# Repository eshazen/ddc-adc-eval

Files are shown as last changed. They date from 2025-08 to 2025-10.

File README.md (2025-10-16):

# ddc-adc-eval

Evaluation board for DDC112 ADC (Arduino UNO shield?).
See `led-photodiode-avr` design for working board.

## Notes from DDC112 datasheet:

* CLK freq range 1-10MHz
* Can generate 8MHz easily using AVR CTC
  <br>Conversion rate then 1.6kHz max
* It is recommended CONV toggle within ±10ns of the rising edge of CLK
* Mode (Cont vs Ncont) selected by state of CONT pin at power-up
  <br>can also switch based on T(INT): space between CONV edges > 4794 clocks
  (600uS at 8MHz clock)
* Data ready at ~526uS at 8MHz (4208 clocks)

## Readout strategy

* Readout function takes ~32us for 20 bits
* So maybe use CONV period of 558 + 10us (568us or 4544 clocks - 9088 period)

## Version 2 ECOs

### Main board

* Add transistors, expand to support 8 LEDs
* Change to common anode configuration (incl connector pinout)
* Correct external caps on DDC (2 -> 4 C's)
* Add 12 bit ADC for temperature sensor
* Testpoints?

### Optical board

* Fix photodiode pinout
* Add temp sensor next to photodiode on copper pad
* Add two Marubeni footprints next to D1 and D3
* Wire 8 LED drivers to the 9 LEDs with a jumper to choose between e.g. D3 and one Marubeni channel.
* Change to common anode topology
*

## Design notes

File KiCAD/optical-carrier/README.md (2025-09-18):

# optical-carrier

Simple carrier board for one photodiode and 3 LEDs.

## ECOs

* Photodiode wiring is reversed from the "obvious" orientation.

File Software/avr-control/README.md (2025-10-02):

# avr-control

Interactive CLI for testing the hardware.
This version uses interrupt-driven UART transmit to allow
continuous data acquisition.
```
    T [n]         - start timers with CONV period=n default 10000
    G n           - set integrator range 0-7
    C n           - enable/disable charge test mode
    A [d [a]]     - stream data at 800/d Hz average a samples
    L d           - set LEDs
    R             - read ADC repeatedly
    P             - read ADC and print
    D n           - set DAC
    M en ch       - set mux en=0/1 ch=0..7
    F             - capture fast and display
    ---
    W t r [d...]  - write I2C
```
Some notes:

* 'A' has a few options:
```
    A          output at default 1Hz, average 800 samples
	A 100      output at 800/100 = 8Hz, average 100 samples
	A 800 1    output at 1Hz, no averaging
```
* 'P' captures and displays data at about 1HZ.
<br>It always captures with the same phase of CONV
* 'F' captures 100 samples at the max rate continuously
<br>When any UART rx is seen, it stops and dumps the data
<br>The last column is the state of CONV (integrator A/B)

## Enhancements for further testing

Readout rate with T = 10000 should be exactly 1.6kHz.

After discussion with Lina:

New readout mode.  Variable rate from 100Hz to .02Hz.
Average up to 2^12 samples.

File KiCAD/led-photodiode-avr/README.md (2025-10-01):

# led-photodiode-avr

This is a test board with a 3-channel constant-current LED driver,
two-channel DDC112 ADC and an ATMega328 MCU.

An interactive CLI for testing is available in
`software/avr-clock-test`.

## Testing

Board#1 is in Lina's hands

Board#2 stuffing

* C1, C15 MIA so installed 0.47uF in place of 0.33uF

Running now.

T = 9800 works well

## ECOs

* External cap wiring incorrect.  For channel 1 two caps are needed,
on pins (3,4) and (5,6).  Same for channel 2

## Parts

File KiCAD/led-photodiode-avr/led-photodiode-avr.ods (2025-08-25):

Reference | Qty | Value | DNP | DigikeyNumber | ManufacturerNumber | 3xQty | OrderQty
C1,C15 | 2 | 0.33uF |  | 1276-1123-1-ND | CL21B334KBFNNNE | 6 | 10
C2,C4,C7,C9,C11,C13 | 6 | 10uF |  | 1292-0805X106K250CT-ND | 0805X106K250CT | 18 | 20
C3,C8 | 2 | 22uF |  | 1276-CL21A226MAYNNNECT-ND | CL21A226MAYNNNE | 6 | 10
C5,C6,C10,C12,C14,C16,C18,C22,C23,C54,C55 | 11 | 0.1uF |  | 478-KGM21NR71H104KTCT-ND | KGM21NR71H104KT | 33 | 50
C17 | 1 | 120pF |  | 399-C0805C121J3GACTUCT-ND | C0805C121J3GACTU | 3 | 10
C21 | 1 | 1nF |  | 399-C0805C102J5GACTUCT-ND | C0805C102J5GACTU | 3 | 10
C52 | 1 | 1.0uF |  | 1276-1029-1-ND | CL21B105KBFNNNE | 3 | 10
D1,D2,D3 | 3 | LED |  | 1516-QBLP631-R3ACT-ND | QBLP631-R3A | 9 | 15
J1 | 1 | Screw_Terminal_01x02 |  | A98076-ND | 282836-2 | 3 | 3
J2 | 1 | Conn_02x08_Odd_Even |  | 10129381-916001BLF-ND | 10129381-916001BLF | 3 | 3
J3 | 1 | ISP |  | 952-2092-ND | M20-9950345 | 3 | 3
L1,L2 | 2 | 10uH |  | 445-6762-1-ND | MLZ2012N100LT000 | 6 | 10
Q1,Q2,Q3,Q4 | 4 | TTC1949 |  | TTC1949-GRLFCT-ND | TTC1949-GR,LF | 12 | 12
R1 | 1 | 10k |  | P10KACT-ND | ERJ-6GEYJ103V | 3 | 10
R2,R10,R47 | 3 | 1.5k |  | 541-4161-1-ND | CRCW08051K50FKEAC | 9 | 20
R3,R5,R6 | 3 | 1k |  | 541-1.00KCCT-ND | CRCW08051K00FKEA | 9 | 20
R4 | 1 | 442 |  | 311-442CRCT-ND | RC0805FR-07442RL | 3 | 10
R7 | 1 | 24.9 |  | 541-CRCW120624R9FKEAHPCT-ND | CRCW120624R9FKEAHP | 3 | 10
R8,R9,R45 | 3 | 4.7k |  | 541-4131-1-ND | CRCW08054K70FKEAC | 9 | 20
U1 | 1 | REF3040AIDBZT |  | REF3040AIDBZTCT-ND | REF3040AIDBZT | 3 | 3
U2,U10 | 2 | AZ1117CH2-5.0 |  | 31-AZ1117CH2-5.0TRG1CT-ND | AZ1117CH2-5.0TRG1 | 6 | 10
U5 | 1 | DDC112 |  | 296-DDC112U/1KCT-ND | DDC112U/1K | 3 | 3
U6 | 1 | LTC1380 |  | 505-LTC1380CS#PBF-ND | LTC1380CS#PBF | 3 | 5
U7 | 1 | ATmega328-A |  | ATMEGA328P-AU-ND | ATMEGA328P-AU | 3 | 3
U8, U3 | 2 | OPA365AIDR |  | 296-46162-1-ND | OPA365AIDR | 6 | 6
U9 | 1 | LTC2631 |  | LTC2631CTS8-HZ12#TRMPBFCT-ND | LTC2631CTS8-HZ12#TRMPBF | 3 | 3
Y1 | 1 | CO_16MHZ |  | XC1899CT-ND | ECS-3961-160-AU-TR | 3 | 3

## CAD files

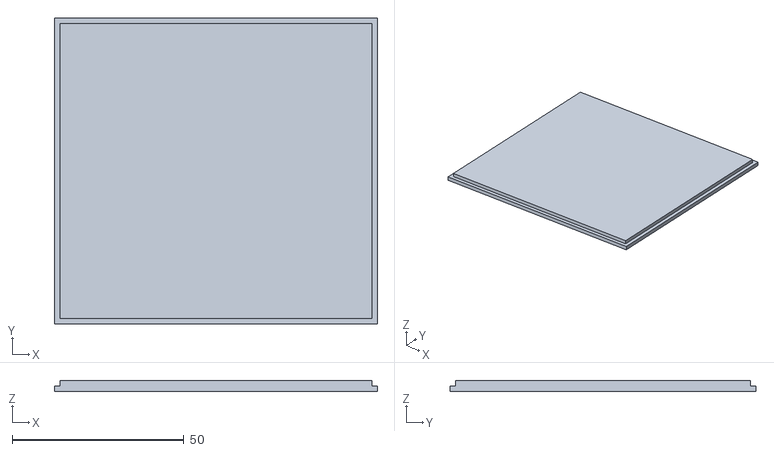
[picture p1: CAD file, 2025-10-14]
Box/adc_lid.stl
94.0 x 88.9 x 3.10

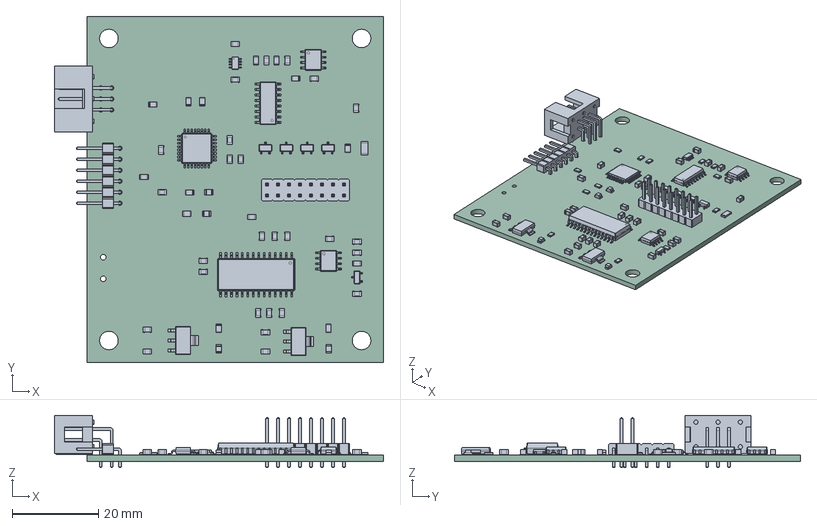
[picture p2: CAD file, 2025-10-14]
KiCAD/led-photodiode-avr/led-photodiode-avr.step
76.1 x 80.0 x 12.1 mm
L_0805_2012Metric x 2
SC-59 x 4
C_0805_2012Metric x 26
R_0805_2012Metric x 13
SOIC-8_3.9x4.9mm_P1.27mm x 2
PinHeader_1x06_P2.54mm_Horizontal
SOT-223 x 2
SOIC-28W_7.5x17.9mm_P1.27mm
SOT-23
SOIC-16_3.9x9.9mm_P1.27mm
LED_0805_2012Metric x 4
optical-carrier
IDC-Header_2x03_P2.54mm_Horizontal
PinHeader_2x08_P2.54mm_Vertical
TSOT-23-8
TQFP-32_7x7mm_P0.8mm
R_1206_3216Metric
led-photodiode-avr_PCB

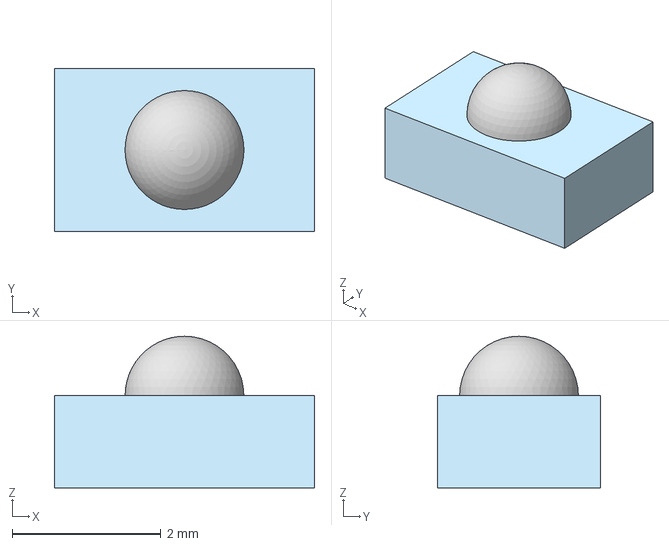
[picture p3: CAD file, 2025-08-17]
KiCAD/optical-carrier/models/LED_MTE9730.step
3.50 x 2.20 x 2.04 mm
Surface 1

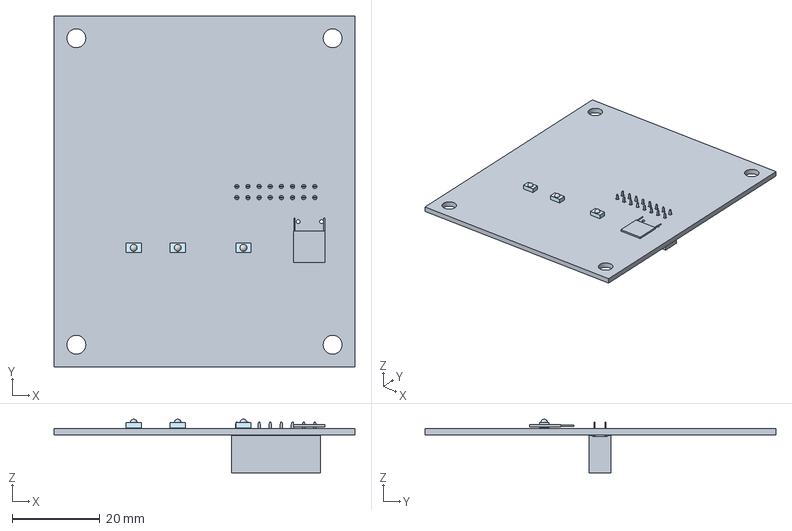
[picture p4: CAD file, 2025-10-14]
KiCAD/optical-carrier/optical-carrier.step
68.6 x 80.0 x 12.3 mm
Surface 1 x 3
PinSocket_2x08_P2.54mm_Vertical
optical-carrier_PCB

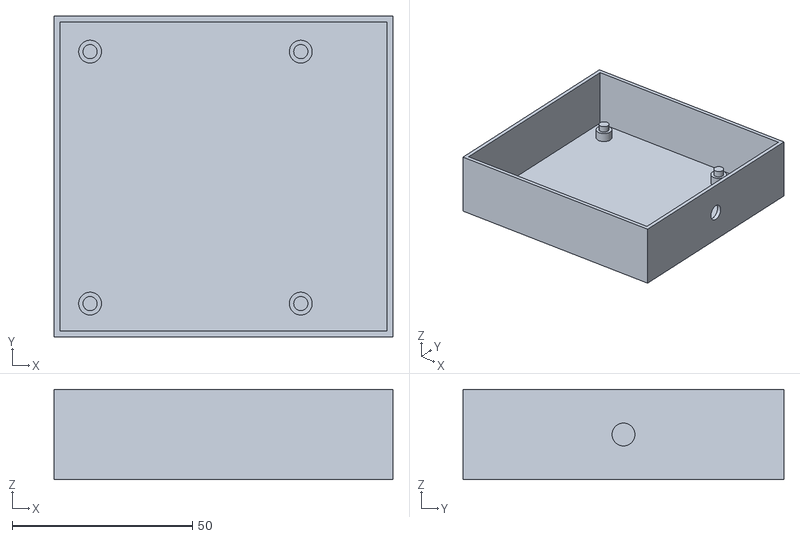
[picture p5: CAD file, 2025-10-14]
Box/adc_box.stl
94.0 x 88.9 x 25.0

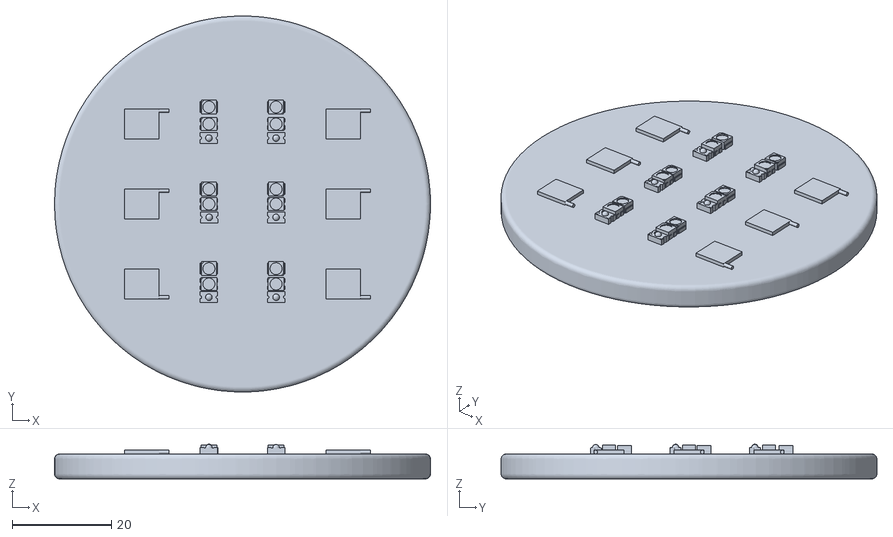
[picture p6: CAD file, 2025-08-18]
KiCAD/led-photodiode-avr/models/OptodeCell_081425.STL
75.6 x 75.6 x 6.97

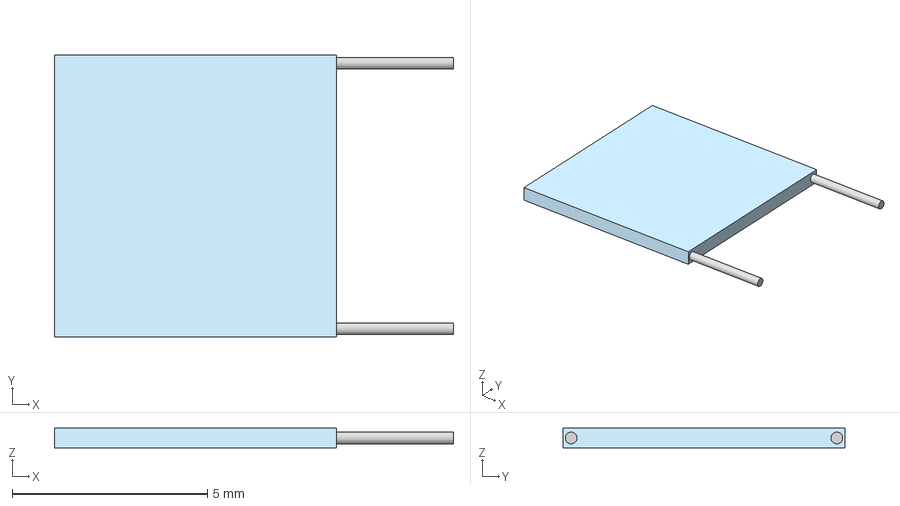
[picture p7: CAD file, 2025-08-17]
KiCAD/optical-carrier/models/Photodiode.step
10.2 x 7.21 x 0.5 mm

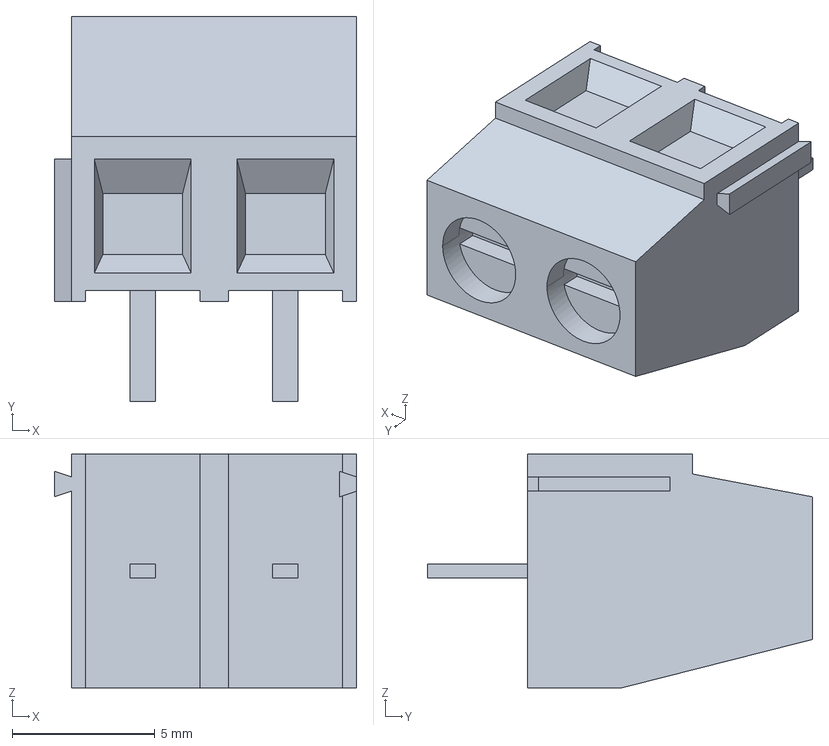
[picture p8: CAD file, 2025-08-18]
KiCAD/led-photodiode-avr/models/282836-2.step
10.6 x 13.5 x 8.20 mm

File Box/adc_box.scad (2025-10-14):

//
// simple dark box for DDS test rig
//


mm = 25.4;
$fn = 32;
e = 0.1;

pcb_w = 2.7*mm;
pcb_l = 3.15*mm;

hole_dx = 2.3*mm;
hole_dy = 2.75*mm;
peg_dia = 0.155*mm;
so_hgt = 0.15*mm;
peg_len = 2.5;

box_w = 3.7*mm;
box_l = 3.5*mm;
box_t = 1.6;
box_h = 25;

module standoff_at( x, y, dia, hole, hgt, rot) {
    translate( [x, y, 0]) {
      rotate( [0, 0, rot]) {
      difference() {
	cylinder( d=dia, h=hgt);
	translate( [0, 0, -e])
	  cylinder( d=hole, h=hgt+2*e);
      }
    }
  }
}

module standoff_at_peg( x, y, dia, peg, hgt, peg_len) {
  translate( [x, y, 0]) {
    cylinder( d=dia, h=hgt);
    translate( [0, 0, hgt-e])
      cylinder( d=peg, h=peg_len+e);
  }
}

module standoffs() {
  standoff_at_peg( 0, hole_dy, 0.25*mm, peg_dia, so_hgt, peg_len);
  standoff_at_peg( 0, 0, 0.25*mm, peg_dia, so_hgt, peg_len);
  standoff_at_peg( hole_dx, 0, 0.25*mm, peg_dia, so_hgt, peg_len);
  standoff_at_peg( hole_dx, hole_dy, 0.25*mm, peg_dia, so_hgt, peg_len);
  //  translate( [-0.2*mm, -0.2*mm, 0]) color("red") cube( [pcb_w, pcb_l, 1.6]);
}

module box( wid, leng, hgt, thick) {
  difference() {
    cube( [wid, leng, hgt]);
    translate( [thick, thick, thick])
      cube( [wid-2*thick, leng-2*thick, hgt]);
    rotate( [90, 0, 90])
      translate( [box_l/2, box_h/2, box_l])
      cylinder( d=0.25*mm, h=10);
  }
}

module box_assy() {
  box( box_w, box_l, box_h, box_t);
  translate( [10, (box_w-pcb_w)/2-0.2*mm+box_t, box_t-e])
    standoffs();
}

module lid() {
  cube( [box_w, box_l, box_t]);
  translate( [box_t, box_t, -box_t+e])
    cube( [box_w-box_t*2, box_l-box_t*2, box_t]);
}

 box_assy();
// rotate( [0, 180, 0]) lid();

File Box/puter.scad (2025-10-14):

//
// car computer enclosure
//

mm = 25.4;
$fn = 32;
e = 0.1;

include <oled.scad>

//
// case body
//
// body_spc = 0.05*mm;
body_spc = 0.075*mm;

body_w = 6.875*mm-body_spc;
body_h = 2.125*mm-body_spc;

//--- normal
//body_d = 2.5*mm;
//pcb_standoff_down = 0.25*mm + 0.7*mm;
//--- fast print
body_d = 10;     /* fast print */
pcb_standoff_down = 2;

body_thk = 1.6;
body_lip = 2.0;

panel_w = body_w + 2*body_lip;
panel_h = body_h + 2*body_lip;

panel_w_in = body_w-2*body_thk;
panel_h_in = body_h-2*body_thk;

// PCB mounting holes
pcb_hole_dx = 6.25*mm;
pcb_hole_dy = 1.5*mm;
// pcb_hole_dia = 0.098*mm;	/* 4-40 tap drill */
pcb_hole_dia = 0.140*mm;	/* 6-32 test fit */
pcb_standoff_dia = 0.25*mm;


panel_hole_dia = 0.15*mm;

pcb_so_supp_wid = 3;
pcb_so_supp_len = pcb_hole_dia/2+6-body_spc/2;

module standoff_at( x, y, dia, hole, hgt, rot) {
    translate( [x, y, 0]) {
      rotate( [0, 0, rot]) {
      difference() {
	union() {
	  cylinder( d=dia, h=hgt);
	  translate( [-pcb_so_supp_wid/2, -pcb_so_supp_len, 0])
	    cube( [pcb_so_supp_wid, pcb_so_supp_len, hgt]);
	}
	translate( [0, 0, -e])
	  cylinder( d=hole, h=hgt+2*e);
      }
    }
  }
}

// draw box with lip, centered
module box() {
     translate( [-body_w/2, -body_h/2, -body_d])
     difference() {
	  union() {
	       // box body
	       cube( [body_w, body_h, body_d]);
	       // lip
	       translate( [-body_lip, -body_lip, body_d-body_thk])
		    cube( [body_w+2*body_lip, body_h+2*body_lip, body_thk]);
	  }
	  // cavity
	  translate( [body_thk, body_thk, body_thk])
	       cube( [body_w-2*body_thk, body_h-2*body_thk, body_d]);
	  // wiring hole
	  translate( [4*body_w/5, body_h/2, -e])
	       cylinder( d=0.375*mm, h=10);
	  echo("Cavity (mm)", body_w-2*body_thk, body_h-2*body_thk, body_d);
	  echo("Cavity (in)", (body_w-2*body_thk)/mm, (body_h-2*body_thk)/mm, body_d/mm);
     }

     translate( [0, 0, -body_d+body_thk-e]) {
       standoff_at( -pcb_hole_dx/2, -pcb_hole_dy/2, pcb_standoff_dia, pcb_hole_dia, body_d-pcb_standoff_down, 270); 
       standoff_at( -pcb_hole_dx/2, pcb_hole_dy/2, pcb_standoff_dia, pcb_hole_dia, body_d-pcb_standoff_down, 270);
       standoff_at( pcb_hole_dx/2, -pcb_hole_dy/2, pcb_standoff_dia, pcb_hole_dia, body_d-pcb_standoff_down, 90); 
       standoff_at( pcb_hole_dx/2, pcb_hole_dy/2, pcb_standoff_dia, pcb_hole_dia, body_d-pcb_standoff_down, 90);
    }
}

module mounting_holes() {
  translate( [-pcb_hole_dx/2, -pcb_hole_dy/2, 0]) cylinder( h=20, d=panel_hole_dia);
  translate( [-pcb_hole_dx/2, pcb_hole_dy/2,  0]) cylinder( h=20, d=panel_hole_dia);
  translate( [pcb_hole_dx/2, -pcb_hole_dy/2,  0]) cylinder( h=20, d=panel_hole_dia);
  translate( [pcb_hole_dx/2, pcb_hole_dy/2, 0]) cylinder( h=20, d=panel_hole_dia);
}


// front panel, centered

module panel() {
  translate( [-panel_w/2, -panel_h/2, 0]) {
    cube( [panel_w, panel_h, body_thk]);
    translate( [body_lip+body_thk, body_lip+body_thk, -body_thk+e])
      cube( [panel_w_in, panel_h_in, body_thk]);
  }
     
}

// holes for switches, knob, LEDs, USB
module button_holes() {
  // LEDs
  translate( [-115, 35, 0])  
    cylinder( d=3.5, h=20);
  translate( [-108, 35, 0])  
    cylinder( d=3.5, h=20);
  // knob
  translate( [-114, 18.5, 0])
    cylinder( d=17, h=20);
  // left 2 switches
  cube( [18, 38, 20]);
  // USB
  translate( [12.7, -6.5, 0])
    cube( [12, 5, 20]);
}

// translate( [0,0,16]) {
//   difference() {
//     panel();
//     translate( [0, 0, -5]) {
//       translate( [-9,2,0]) oled_holes();
//       mounting_holes();
//       translate( [42.7, -16, 0])
//       button_holes();
//       translate( [panel_w/2-14, 0, 0]) cylinder( h=20, d=0.26*mm);
//     }
//   }
// }


box();

// translate( [0, 0, 5]) {
//      difference() {
//        	  color("brown") panel();
// 	  translate( [-body_w+0.65*mm, 70, 0])
// 	       translate( [147.5, -69.7, 0]) oled_holes();
//      }
// }
// 
// 

// translate( [-body_w+0.62*mm, 71.8, 10]) {
//       color("green") import("car-control.stl");
//       translate( [147.5, -69.9, 3]) oled();
// }

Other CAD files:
Sketches/#SensorBoard.dxf
KiCAD/led-photodiode-avr/photodiode_led.dxf
Sketches/SensorBoard.dxf

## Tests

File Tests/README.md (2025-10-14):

# Testing

### 2025-10-14

`2025-10-14_log_file1.dat` - 10 min run, LED at 2.1V through 10k, gain 1
<br>Cold start, just powered up after weekend

`2025-10-14_log_file2.dat` - 10 min run, LED at 2.6V through 10k, gain 2

`2025-10-14_log_file3.dat` - 10 min run, LED at 2.6V through 10k, gain 1
<br>After an hour or so closed and powered

`2025-10-14_log_file4.dat` - 10 min run, LED at 2.6V through 10k, gain 2
<br>After an hour or so closed and powered

`2025-10-14_log_file10.dat` - Lina's board LED at 2.1V, gain 1
<br>A few min after opening box

`2025-10-14_log_file10.dat` - Lina's board LED at 2.1V, gain 1
<br>3 ohm resistor taped ~1cm from the photodiode.
<br>Turn on at 1W at about sample 200
<br>Off at sample 267

### 2025-10-08

Testing for "Drift" per Lina's results
12:40 Start a run at gain 7 with photodiode in box, bag and lights out

`2025-10-08_log_file1.dat` - 10 minute run.  No trend seen

Try again with red LED in series with 10k at 3.0V.
The level goes up and then down at an apparently linear rate.

`2025-10-08_log_file3.dat` - 60 minute run.
<br>LED off for 1m at 1500s.

Open the box, move things around a bit and start again
Amplitude peaks, then droops at a linear rate for almost 60m

`2025-10-08_log_file4.dat` - 30 minute run.

Initial drop then stable

### 2025-09-11

Here are some waveforms from readout using the software as of 9/11/25.
Initialization is:

    >t 10000
    >g 7
    >p
    
Here is the complete cycle.  Scope channels are:

    1.  CONV
	2.  nDVALID
	3.  DCLK
	4.  DOUT
	
You can see that the digitization frequency is about 1.6kHz and that there is plenty of time to read out the 2x20 bits.

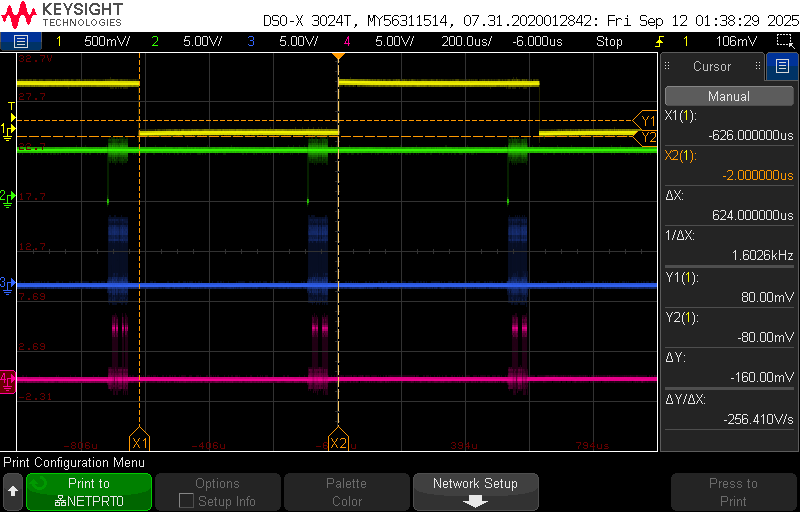
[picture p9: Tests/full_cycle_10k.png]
Full readout


Here is a zoom on the readout portion.

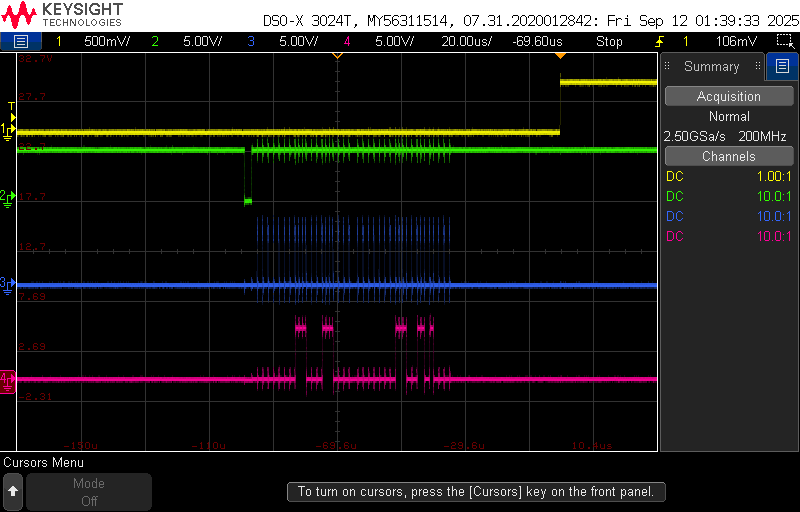
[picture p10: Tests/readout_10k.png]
Readout part


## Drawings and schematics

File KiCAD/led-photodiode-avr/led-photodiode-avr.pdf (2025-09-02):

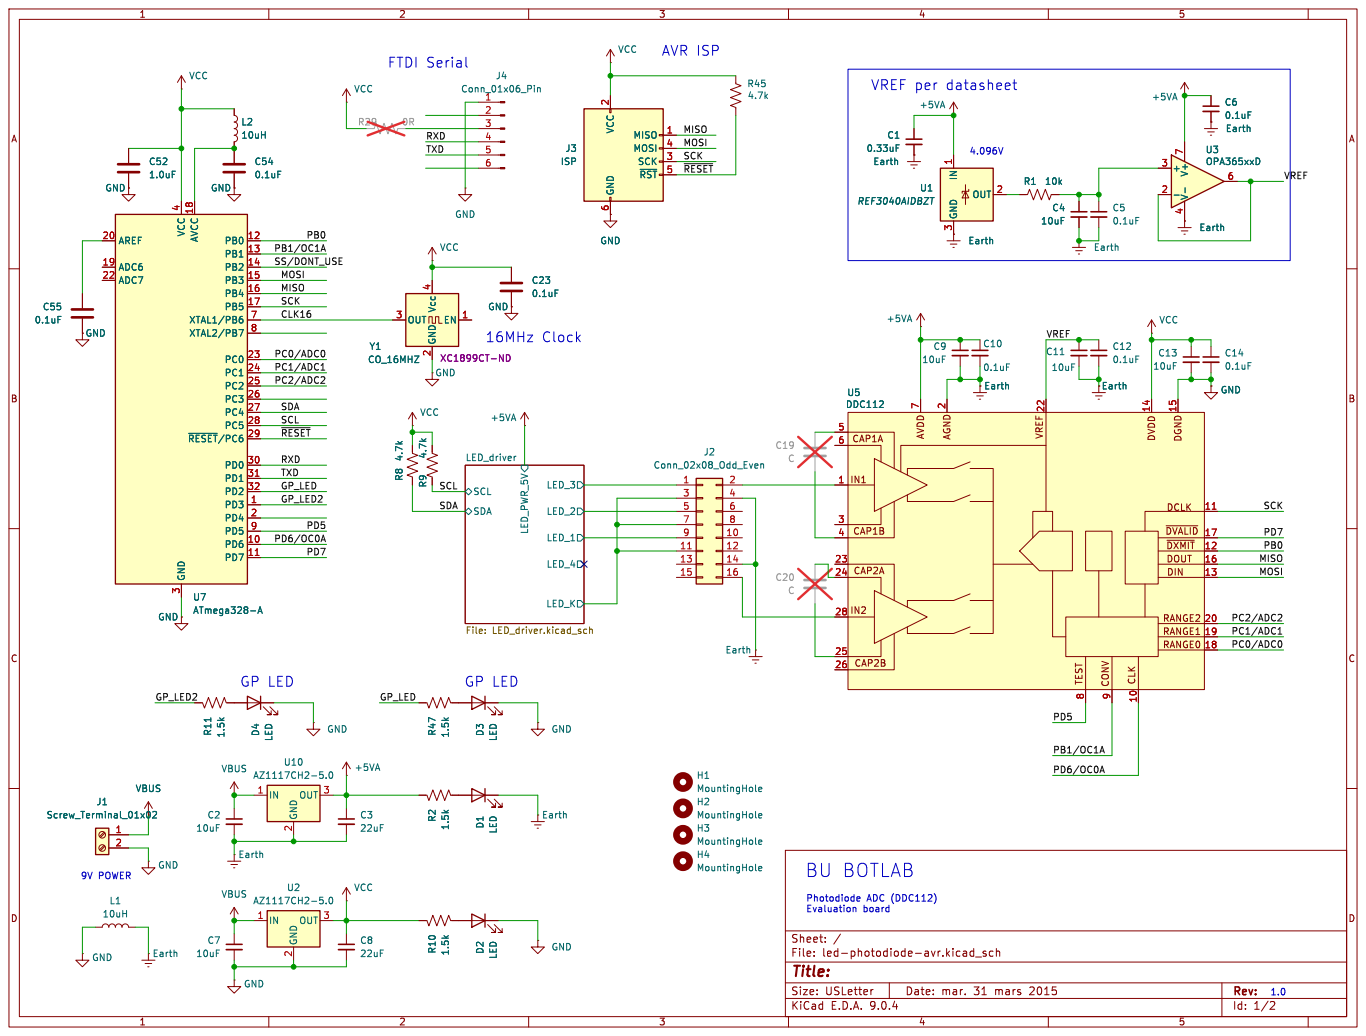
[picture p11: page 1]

6 MISO 1 MOSI 4 SCK 3 ~{RST}5 GND

6 MISO 1 MOSI 4 SCK 3 ~{RST}5

3 OUT 2 Earth GND Earth Earth U5 DDC112

2 OUT 3 U2 AZ1117CH2-5.0 H4 MountingHole H3 MountingHole Earth H1 MountingHole
GP LED

E.D.A. 9.0.4 Size: USLetter | Rev: | D Date: mar. 31 mars 2015 KiCad

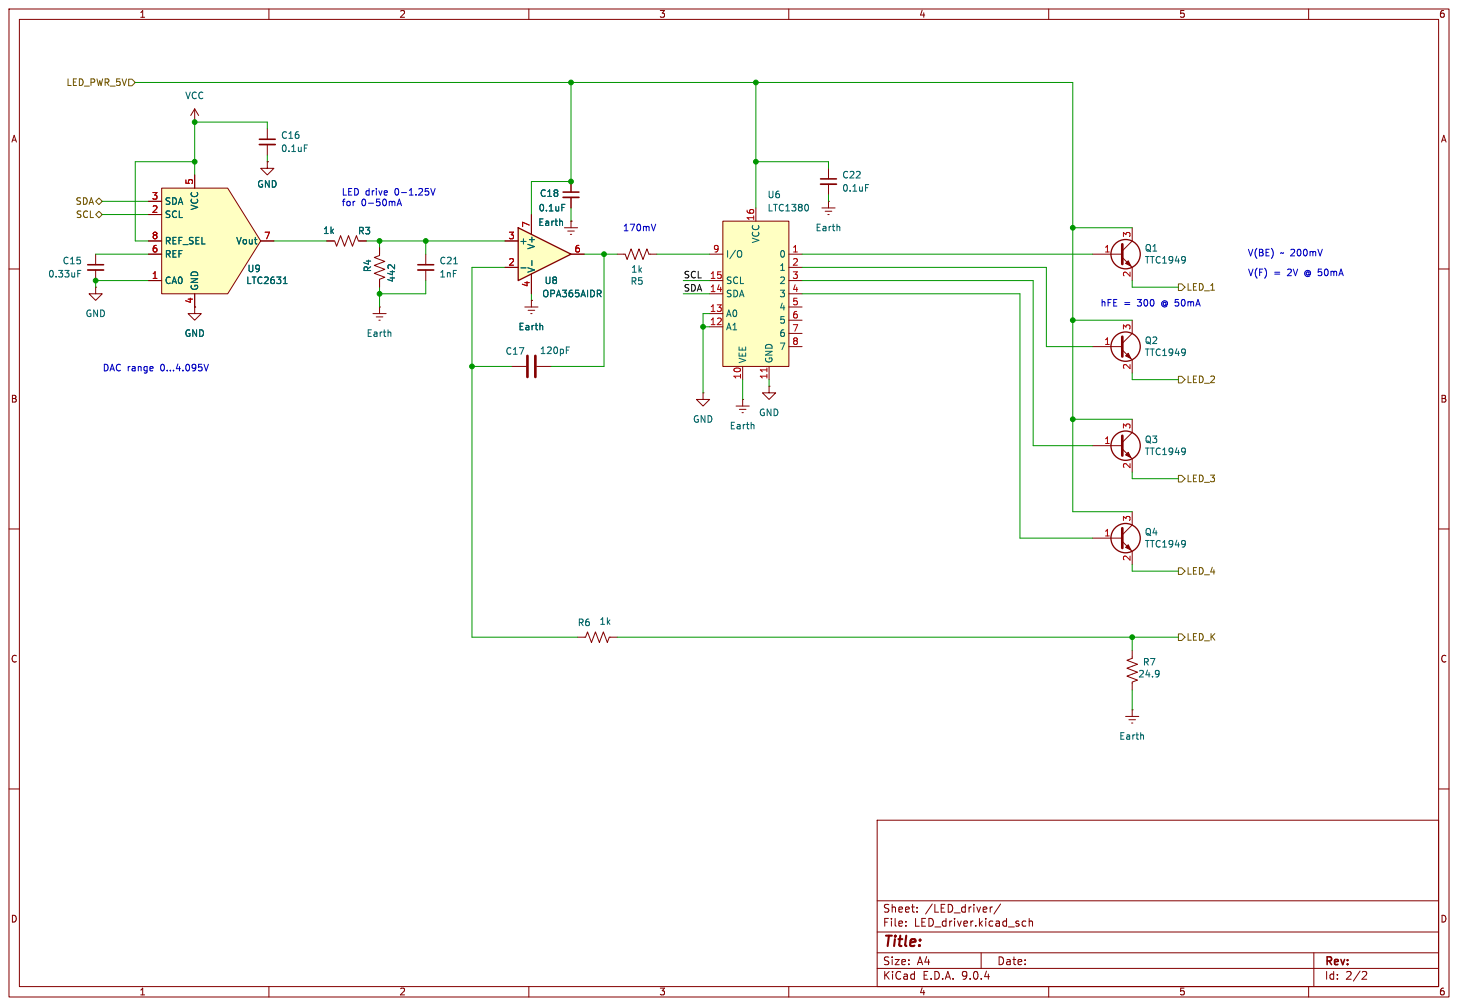
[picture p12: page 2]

Id: 2/2 Title: File: LED_driver.kicad_sch Sheet: /LED_driver/

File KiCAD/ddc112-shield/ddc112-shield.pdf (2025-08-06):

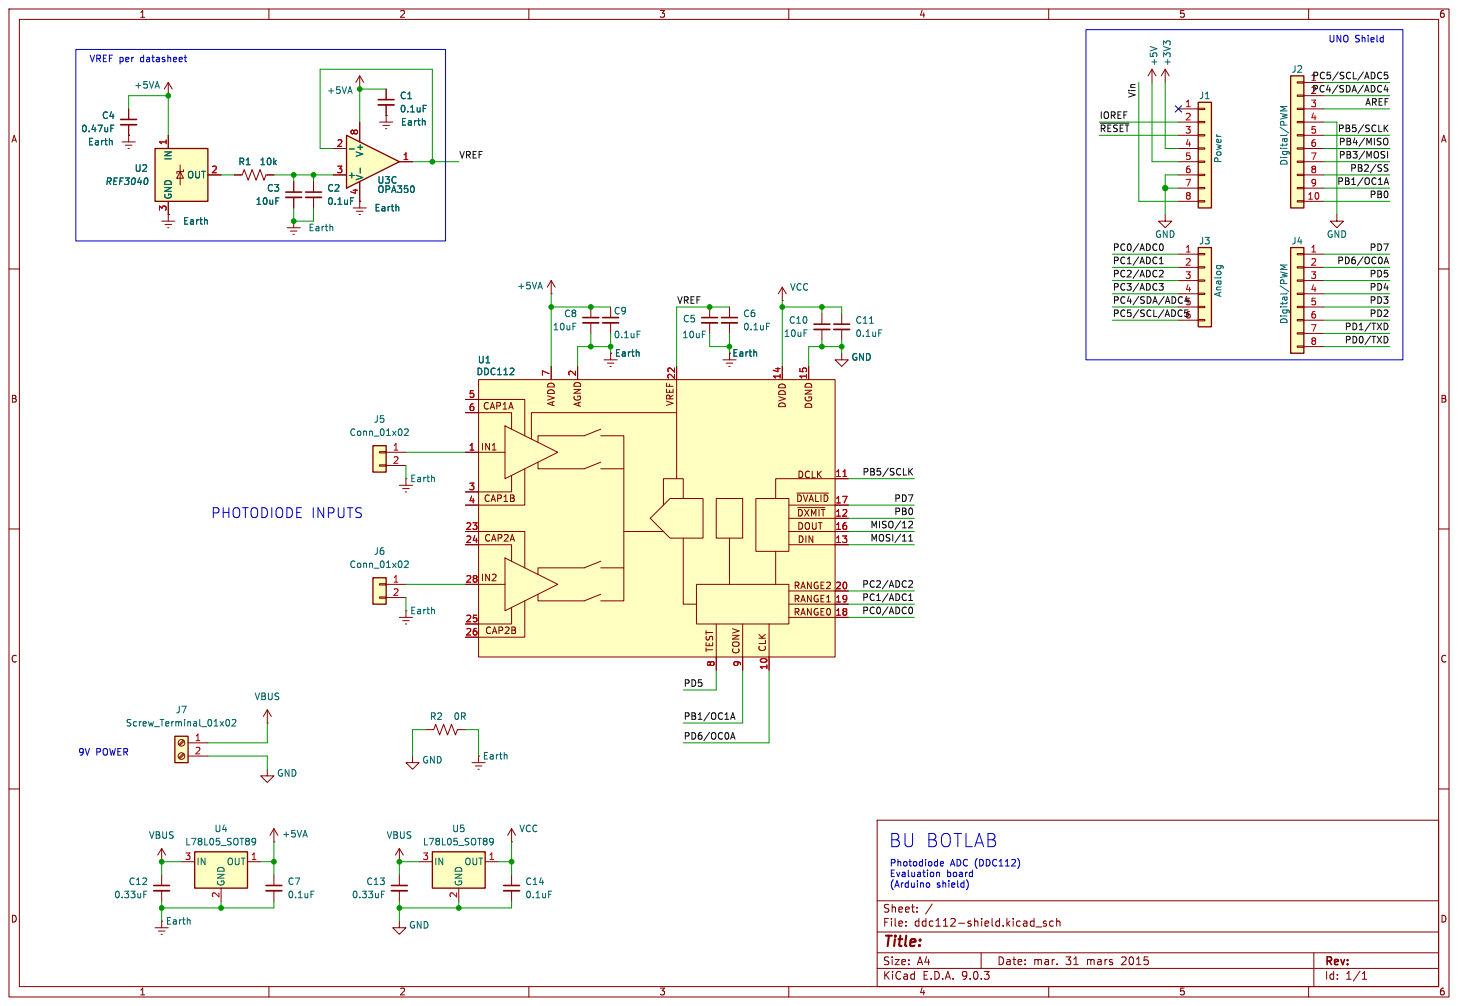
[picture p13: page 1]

(Arduino shield)
Id: 1/1 Title: File: ddc112-shield.kicad_sch Sheet: /

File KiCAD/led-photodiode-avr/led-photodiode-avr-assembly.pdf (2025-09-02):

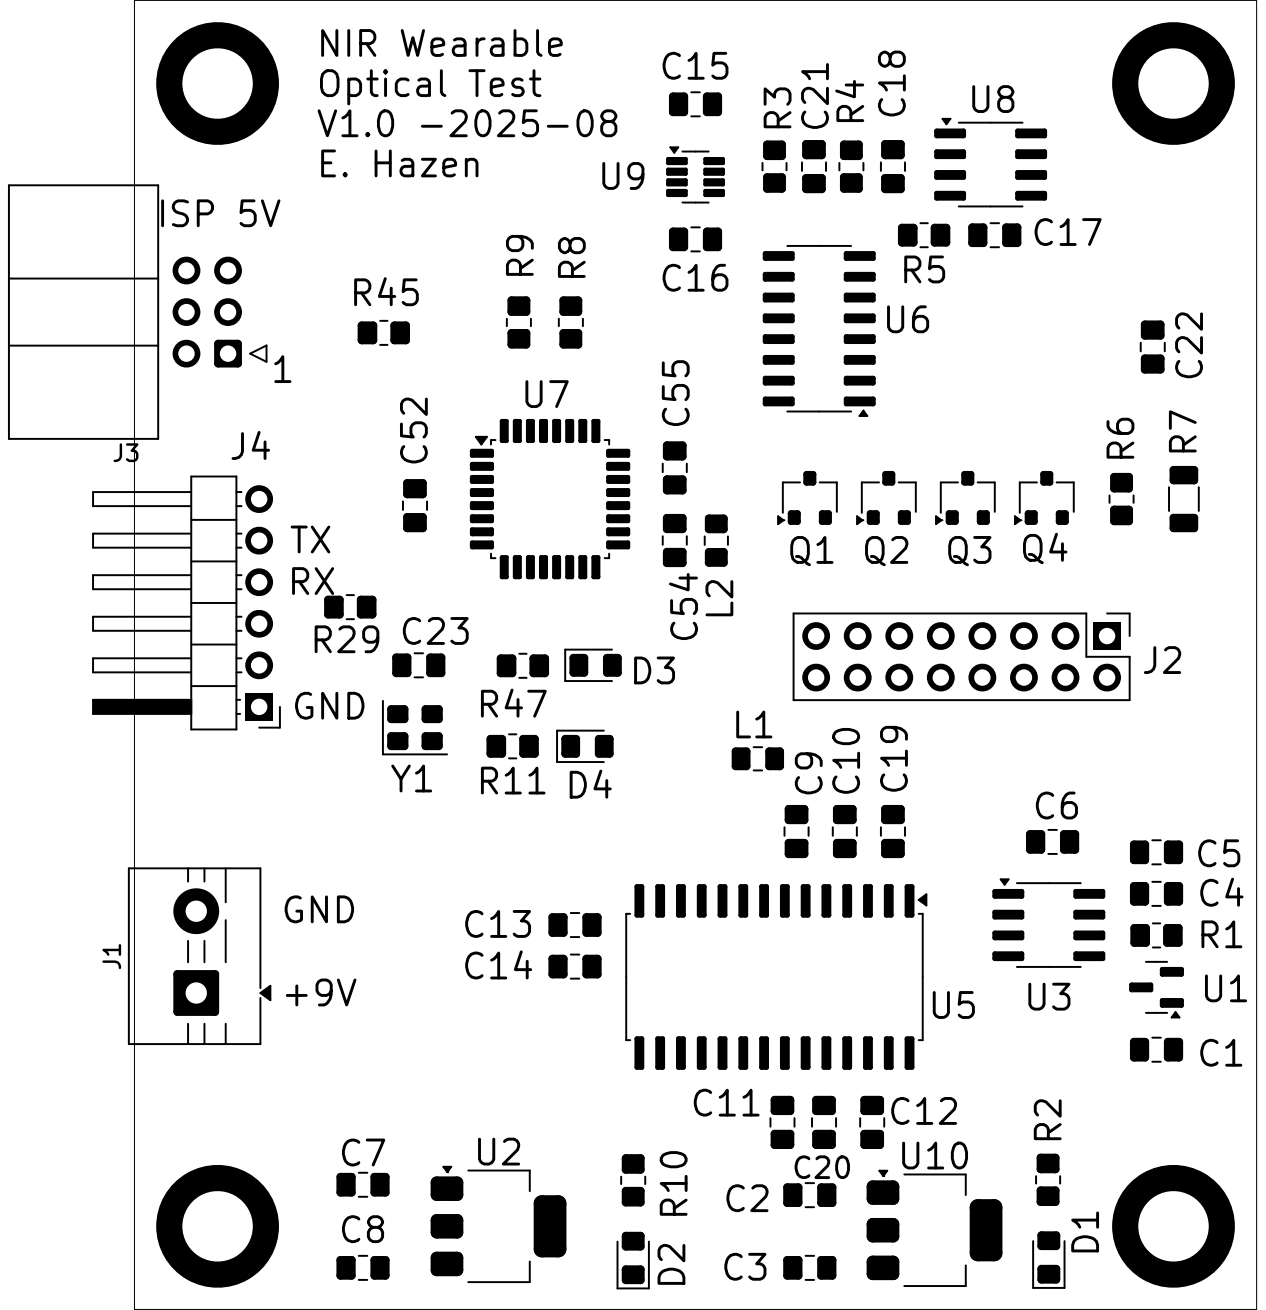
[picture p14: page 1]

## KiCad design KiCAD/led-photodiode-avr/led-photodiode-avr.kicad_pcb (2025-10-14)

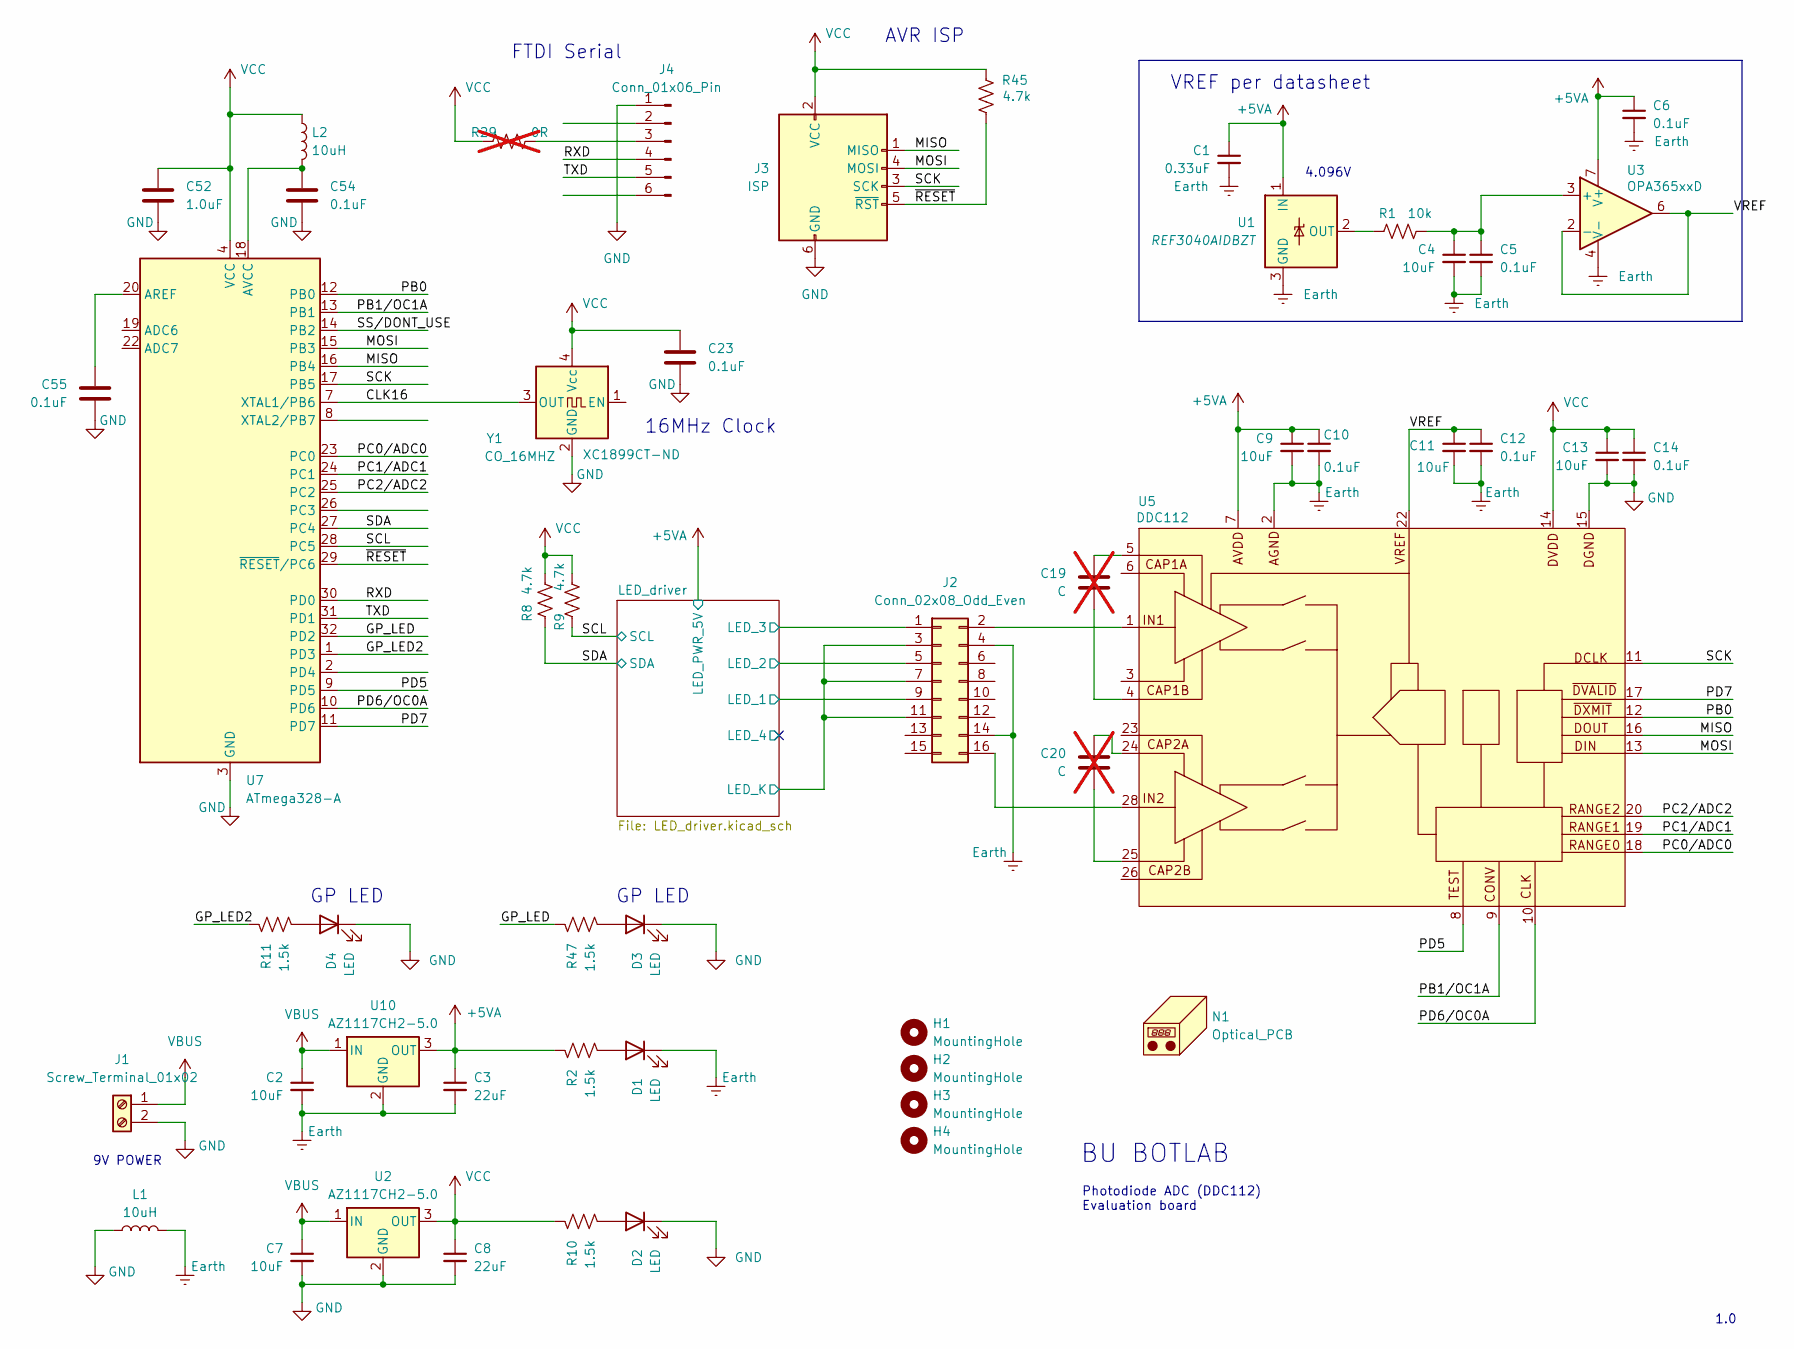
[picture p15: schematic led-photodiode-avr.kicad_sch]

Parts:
C1: 0.33uF; C_0805_2012Metric_Pad1.18x1.45mm_HandSolder; DigikeyNumber 1276-1123-1-ND
C2, C4, C7, C9, C11, C13: 10uF; C_0805_2012Metric_Pad1.18x1.45mm_HandSolder; DigikeyNumber 1292-0805X106K250CT-ND
C3, C8: 22uF; C_0805_2012Metric_Pad1.18x1.45mm_HandSolder; DigikeyNumber 1276-CL21A226MAYNNNECT-ND
C5, C6, C10, C12, C14, C23, C54, C55: 0.1uF; C_0805_2012Metric_Pad1.18x1.45mm_HandSolder; DigikeyNumber 478-KGM21NR71H104KTCT-ND
C19, C20: C; C_0805_2012Metric_Pad1.18x1.45mm_HandSolder; not fitted
C52: 1.0uF; C_0805_2012Metric_Pad1.18x1.45mm_HandSolder; DigikeyNumber 1276-1029-1-ND
D1, D2, D3, D4: LED; LED_0805_2012Metric_Pad1.15x1.40mm_HandSolder; DigikeyNumber 1516-QBLP631-R3ACT-ND
H1, H2, H3, H4: MountingHole; MountingHole_4.3mm_M4_DIN965_Pad
J1: Screw_Terminal_01x02; TerminalBlock_MaiXu_MX126-5.0-02P_1x02_P5.00mm; DigikeyNumber A98076-ND
J2: Conn_02x08_Odd_Even; PinHeader_2x08_P2.54mm_Vertical; DigikeyNumber 10129381-916001BLF-ND
J3: ISP; IDC-Header_2x03_P2.54mm_Horizontal; DigikeyNumber 952-2092-ND
J4: Conn_01x06_Pin; PinHeader_1x06_P2.54mm_Horizontal
L1, L2: 10uH; L_0805_2012Metric_Pad1.15x1.40mm_HandSolder; DigikeyNumber 445-6762-1-ND
N1: Optical_PCB; optical_pcb
R1: 10k; R_0805_2012Metric_Pad1.20x1.40mm_HandSolder; DigikeyNumber P10KACT-ND
R2, R10, R11, R47: 1.5k; R_0805_2012Metric_Pad1.20x1.40mm_HandSolder; DigikeyNumber 541-4161-1-ND
R8, R9, R45: 4.7k; R_0805_2012Metric_Pad1.20x1.40mm_HandSolder; DigikeyNumber 541-4131-1-ND
R29: 0R; R_0805_2012Metric_Pad1.20x1.40mm_HandSolder; not fitted
U1: REF3040AIDBZT; SOT-23; DigikeyNumber REF3040AIDBZTCT-ND
U2, U10: AZ1117CH2-5.0; SOT-223-3_TabPin2; DigikeyNumber 31-AZ1117CH2-5.0TRG1CT-ND
U3: OPA365xxD; SOIC-8_3.9x4.9mm_P1.27mm; DigikeyNumber 296-46162-1-ND
U5: DDC112; SOIC-28W_7.5x17.9mm_P1.27mm; DigikeyNumber 296-DDC112U/1KCT-ND
U7: ATmega328-A; TQFP-32_7x7mm_P0.8mm; DigikeyNumber ATMEGA328P-AU-ND
Y1: CO_16MHZ; Oscillator_SMD_Abracon_ASE-4Pin_3.2x2.5mm; DigikeyNumber XC1899CT-ND

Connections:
+5VA: C1.1, C3.1, C6.1, C9.1, C10.1, R2.1, U1.1 (IN), U3.7 (V+), U5.7 (AVDD), U10.3 (OUT); also elsewhere on the board
/CLK16: U7.7 (XTAL1/PB6), Y1.3 (OUT)
/GP_LED: R47.1, U7.32 (PD2)
/GP_LED2: R11.1, U7.1 (PD3)
/LED_driver/LED_1: J2.9; also elsewhere on the board
/LED_driver/LED_2: J2.5; also elsewhere on the board
/LED_driver/LED_3: J2.1; also elsewhere on the board
/LED_driver/LED_K: J2.3, J2.7, J2.11; also elsewhere on the board
/MISO: J3.1 (MISO), U5.16 (DOUT), U7.16 (PB4)
/MOSI: J3.4 (MOSI), U5.13 (DIN), U7.15 (PB3)
/PB0: U5.12 (~DXMIT), U7.12 (PB0)
/PB1/OC1A: U5.9 (CONV), U7.13 (PB1)
/PC0/ADC0: U5.18 (RANGE0), U7.23 (PC0)
/PC1/ADC1: U5.19 (RANGE1), U7.24 (PC1)
/PC2/ADC2: U5.20 (RANGE2), U7.25 (PC2)
/PD5: U5.8 (TEST), U7.9 (PD5)
/PD6/OC0A: U5.10 (CLK), U7.10 (PD6)
/PD7: U5.17 (~DVALID), U7.11 (PD7)
/RXD: J4.4, U7.30 (PD0)
/SCK: J3.3 (SCK), U5.11 (DCLK), U7.17 (PB5)
/SCL: R9.1, U7.28 (PC5); also elsewhere on the board
/SDA: R8.1, U7.27 (PC4); also elsewhere on the board
/SS/DONT_USE: U7.14 (PB2)
/TXD: J4.5, U7.31 (PD1)
/VREF: C11.1, C12.1, U3.2 (-), U3.6, U5.22 (VREF)
/~RESET: J3.5 (~RST), R45.1, U7.29 (~RESET/PC6)
Earth: C1.2, C2.2, C3.2, C4.2, C5.2, C6.2, C9.2, C10.2, C11.2, C12.2, D1.1 (K), J2.4, J2.14, L1.2, U1.3 (GND), U3.4 (V-), U5.2 (AGND), U5.21 (AGND), U5.27 (AGND), U10.2 (GND); also elsewhere on the board
GND: C7.2, C8.2, C13.2, C14.2, C23.2, C52.2, C54.2, C55.2, D2.1 (K), D3.1 (K), D4.1 (K), J1.2, J3.6 (GND), J4.1, L1.1, U2.2 (GND), U5.15 (DGND), U7.3 (GND), U7.5 (GND), U7.21 (GND), Y1.2 (GND); also elsewhere on the board
unnamed: C19.1, U5.5 (CAP1A)
unnamed: C19.2, U5.4 (CAP1B)
unnamed: C20.1, U5.24 (CAP2A)
unnamed: C20.2, U5.25 (CAP2B)
unnamed: D1.2 (A), R2.2
unnamed: D2.2 (A), R10.2
unnamed: D3.2 (A), R47.2
unnamed: D4.2 (A), R11.2
unnamed: J2.2, U5.1 (IN1)
unnamed: J2.16, U5.28 (IN2)
unnamed: J4.3, R29.2
unnamed: R1.1, U1.2 (OUT)
unnamed: C4.1, C5.1, R1.2, U3.3 (+)
unnamed: C55.1, U7.20 (AREF)
unnamed: C54.1, L2.2, U7.18 (AVCC)
VBUS: C2.1, C7.1, J1.1, U2.1 (IN), U10.1 (IN)
VCC: C8.1, C13.1, C14.1, C23.1, C52.1, J3.2 (VCC), L2.1, R8.2, R9.2, R10.1, R29.1, R45.2, U2.3 (OUT), U5.14 (DVDD), U7.4 (VCC), U7.6 (VCC), Y1.4 (Vcc); also elsewhere on the board

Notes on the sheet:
AVR ISP
FTDI Serial
4.096V
1.0
GP LED
VREF per datasheet
9V POWER
BU BOTLAB
16MHz Clock
Photodiode ADC (DDC112) Evaluation board

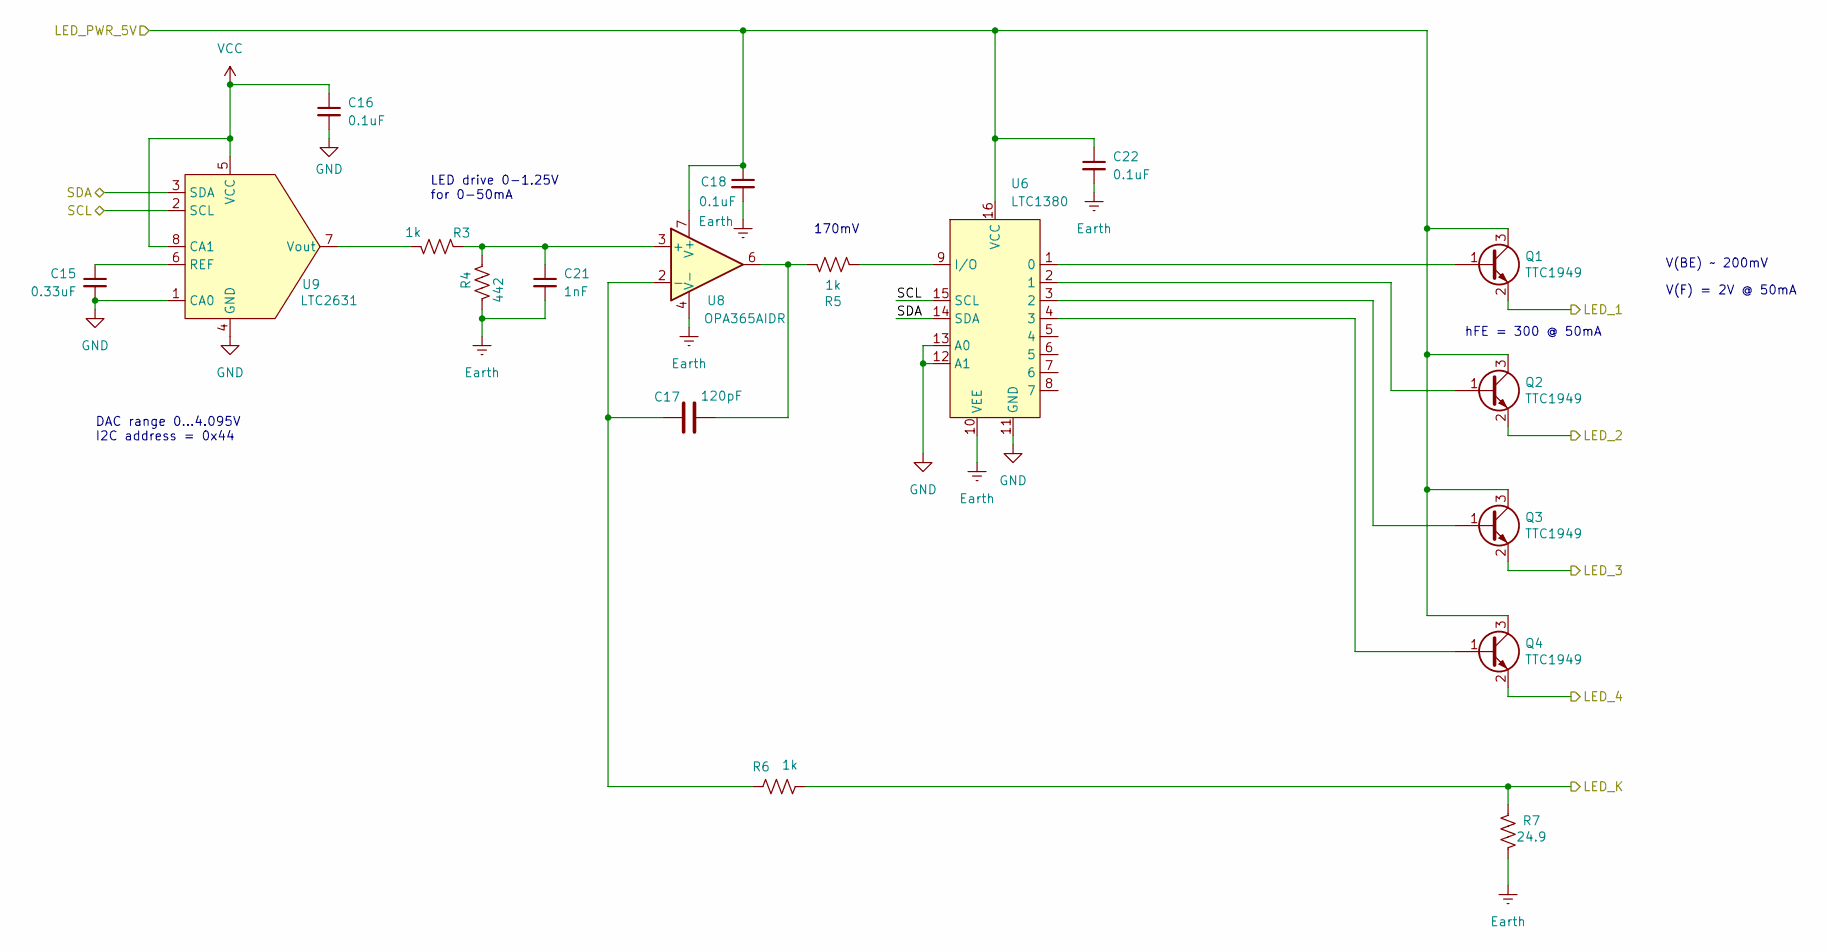
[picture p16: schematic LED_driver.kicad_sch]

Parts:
C15: 0.33uF; C_0805_2012Metric_Pad1.18x1.45mm_HandSolder; DigikeyNumber 1276-1123-1-ND
C16, C18, C22: 0.1uF; C_0805_2012Metric_Pad1.18x1.45mm_HandSolder; DigikeyNumber 478-KGM21NR71H104KTCT-ND
C17: 120pF; C_0805_2012Metric_Pad1.18x1.45mm_HandSolder; DigikeyNumber 399-C0805C121J3GACTUCT-ND
C21: 1nF; C_0805_2012Metric_Pad1.18x1.45mm_HandSolder; DigikeyNumber 399-C0805C102J5GACTUCT-ND
Q1, Q2, Q3, Q4: TTC1949; SC-59; DigikeyNumber TTC1949-GRLFCT-ND
R3, R5, R6: 1k; R_0805_2012Metric_Pad1.20x1.40mm_HandSolder; DigikeyNumber 541-1.00KCCT-ND
R4: 442; R_0805_2012Metric_Pad1.20x1.40mm_HandSolder; DigikeyNumber 311-442CRCT-ND
R7: 24.9; R_1206_3216Metric; DigikeyNumber 541-CRCW120624R9FKEAHPCT-ND
U6: LTC1380; SOIC-16_3.9x9.9mm_P1.27mm; DigikeyNumber 505-LTC1380CS#PBF-ND
U8: OPA365AIDR; SOIC-8_3.9x4.9mm_P1.27mm; DigikeyNumber 296-46162-1-ND
U9: LTC2631; TSOT-23-8; DigikeyNumber LTC2631CTS8-HZ12#TRMPBFCT-ND

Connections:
+5VA: C18.1, C22.1, Q1.3 (C), Q2.3 (C), Q3.3 (C), Q4.3 (C), U6.16 (VCC), U8.7 (V+); also elsewhere on the board
/LED_driver/LED_1: Q1.2 (E); also elsewhere on the board
/LED_driver/LED_2: Q2.2 (E); also elsewhere on the board
/LED_driver/LED_3: Q3.2 (E); also elsewhere on the board
/LED_driver/LED_4: Q4.2 (E)
/LED_driver/LED_K: R6.1, R7.2; also elsewhere on the board
/SCL: U6.15 (SCL), U9.2 (SCL); also elsewhere on the board
/SDA: U6.14 (SDA), U9.3 (SDA); also elsewhere on the board
Earth: C18.2, C21.2, C22.2, R4.2, R7.1, U6.10 (VEE), U8.4 (V-); also elsewhere on the board
GND: C15.2, C16.2, U6.11 (GND), U6.12 (A1), U6.13 (A0), U9.1 (CA0), U9.4 (GND); also elsewhere on the board
unnamed: C17.2, R5.2, U8.6
unnamed: Q1.1 (B), U6.1 (0)
unnamed: Q2.1 (B), U6.2 (1)
unnamed: Q3.1 (B), U6.3 (2)
unnamed: Q4.1 (B), U6.4 (3)
unnamed: R5.1, U6.9 (I/O)
unnamed: C21.1, R3.1, R4.1, U8.3 (+)
unnamed: C17.1, R6.2, U8.2 (-)
unnamed: C15.1, U9.6 (REF)
unnamed: R3.2, U9.7 (Vout)
VCC: C16.1, U9.5 (VCC), U9.8 (CA1); also elsewhere on the board

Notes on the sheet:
DAC range 0...4.095V I2C address = 0x44
LED drive 0-1.25V for 0-50mA
V(BE) ~ 200mV
170mV
V(F) = 2V @ 50mA
hFE = 300 @ 50mA

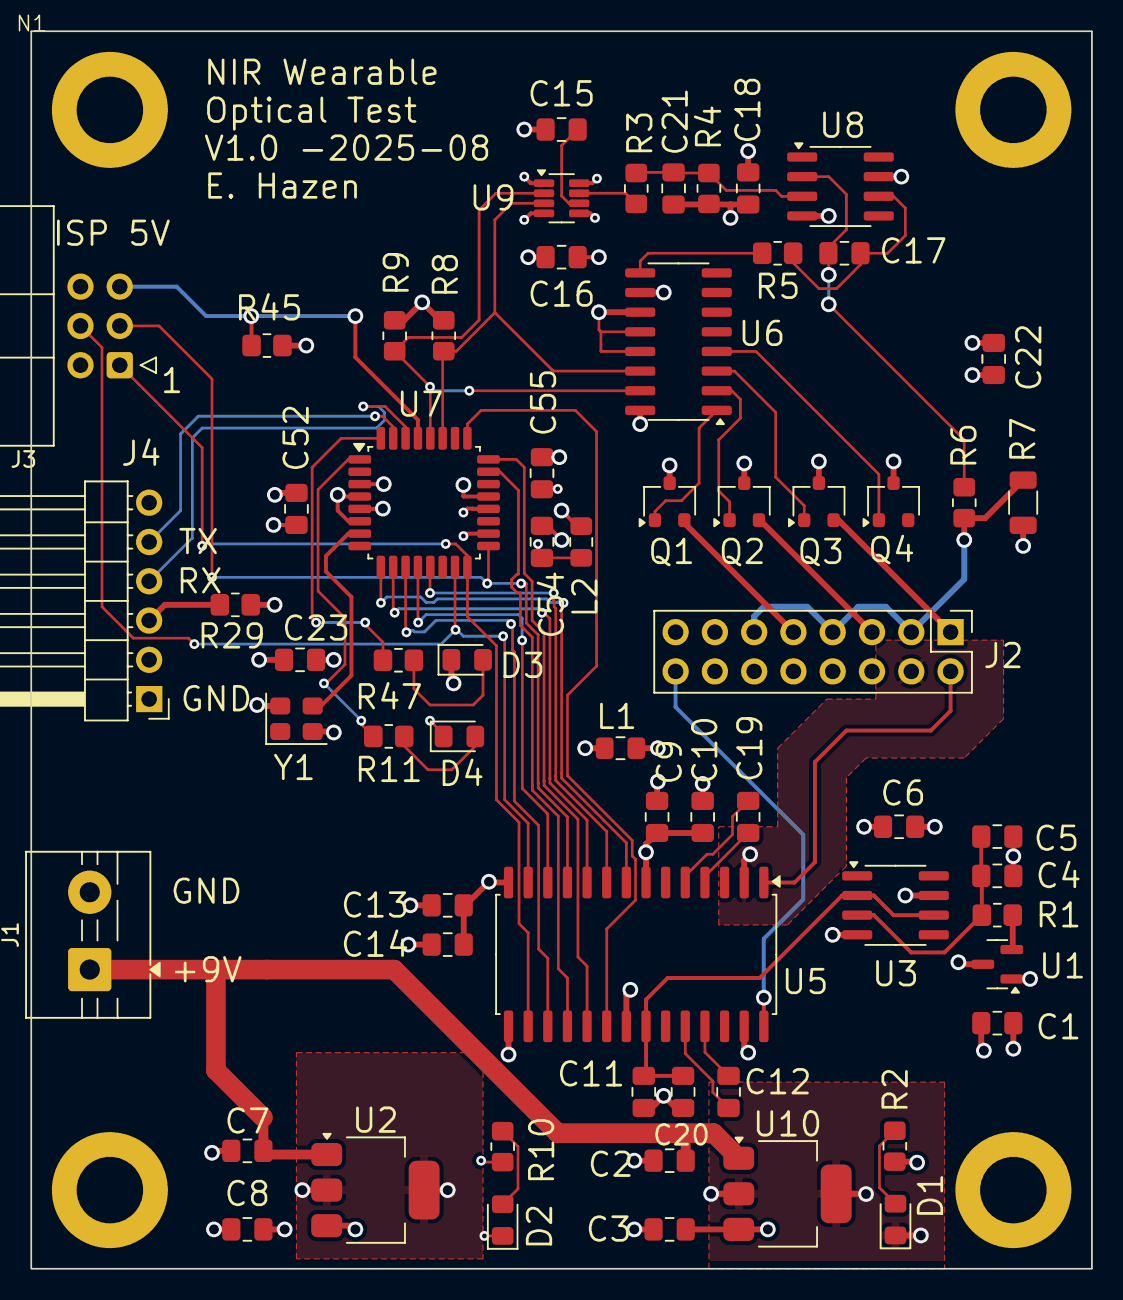
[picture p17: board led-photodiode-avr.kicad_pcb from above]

Board: 4 copper layers, 68.6 x 80.0 mm, 69 parts (0 on the bottom side), 54 nets.

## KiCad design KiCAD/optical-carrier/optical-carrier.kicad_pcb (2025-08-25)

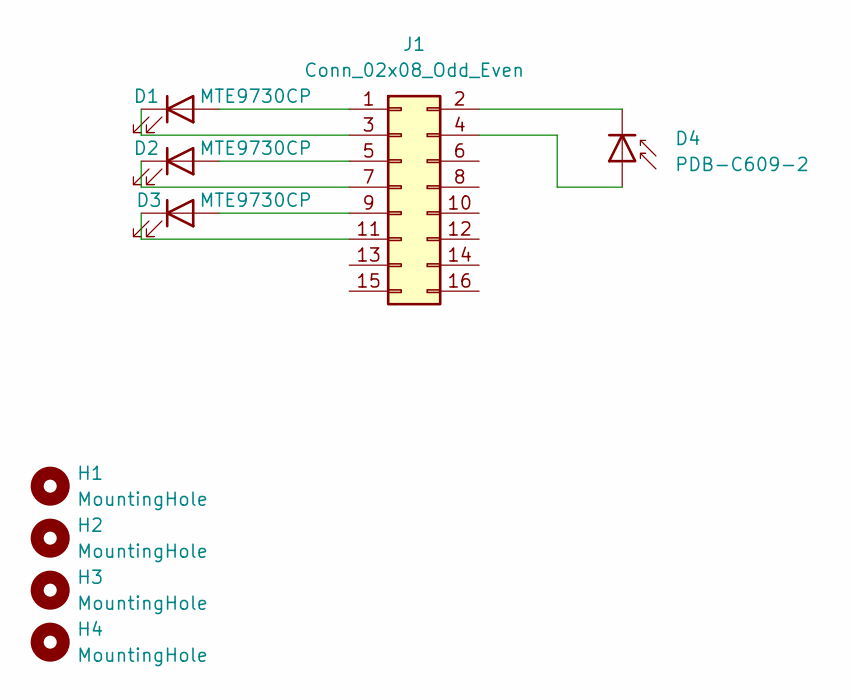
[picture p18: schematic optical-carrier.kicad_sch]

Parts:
D1, D2, D3: MTE9730CP; MTE9730; DigikeyNumber 1125-1435-ND
D4: PDB-C609-2; DigikeyNumber PDB-C609-2-ND
H1, H2, H3, H4: MountingHole
J1: Conn_02x08_Odd_Even; PinSocket_2x08_P2.54mm_Vertical

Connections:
unnamed: D1.2 (A), J1.1
unnamed: D1.1 (K), J1.3
unnamed: D2.2 (A), J1.5
unnamed: D2.1 (K), J1.7
unnamed: D3.2 (A), J1.9
unnamed: D3.1 (K), J1.11
unnamed: D4.2 (A), J1.4
unnamed: D4.1 (K), J1.2

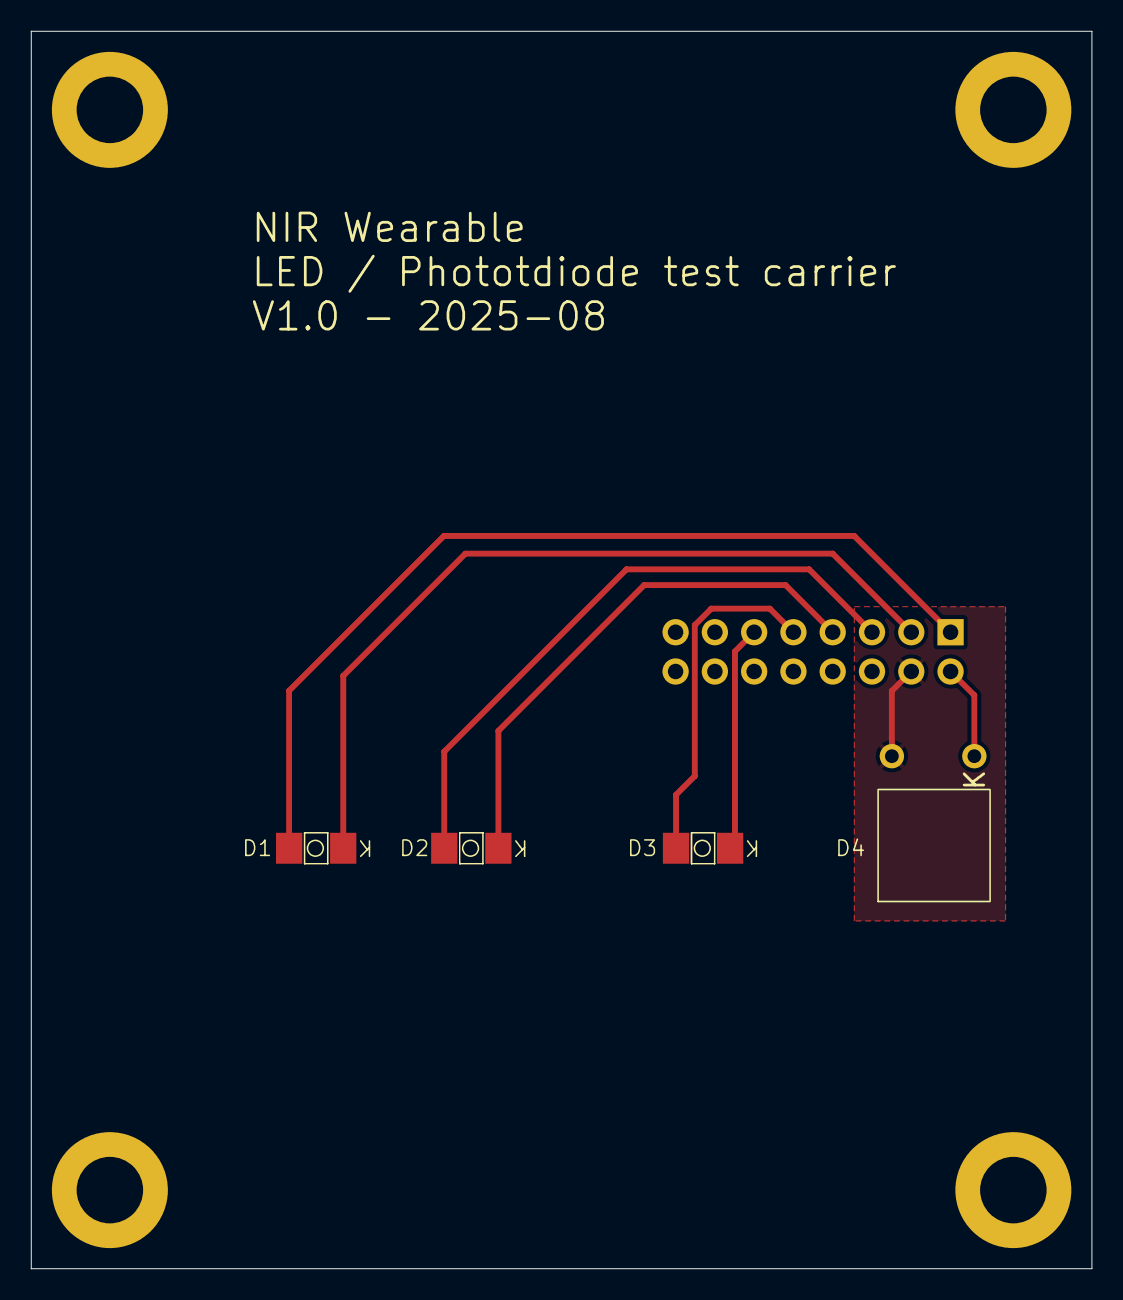
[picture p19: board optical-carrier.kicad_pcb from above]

Board: 2 copper layers, 68.6 x 80.0 mm, 9 parts (1 on the bottom side), 8 nets.

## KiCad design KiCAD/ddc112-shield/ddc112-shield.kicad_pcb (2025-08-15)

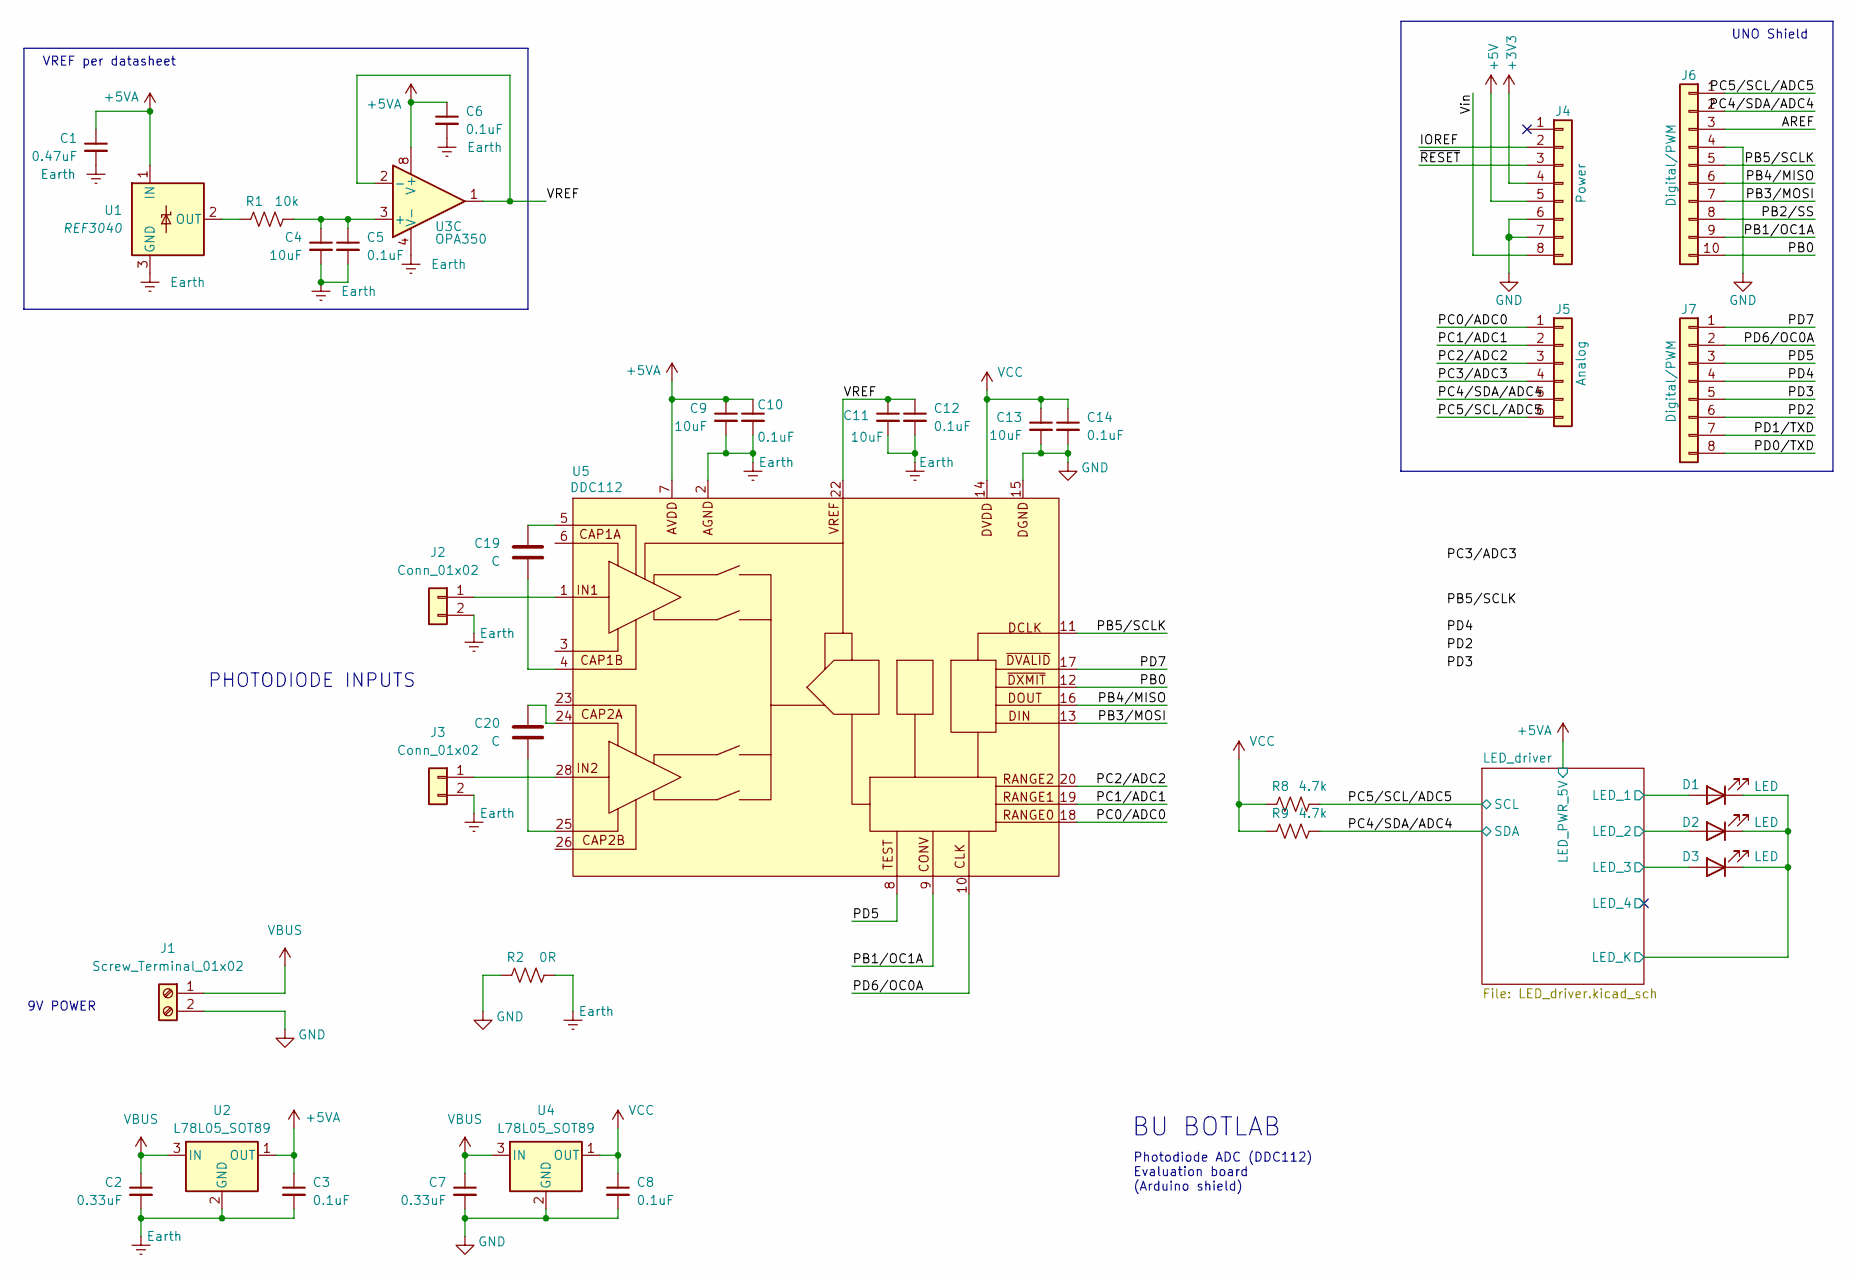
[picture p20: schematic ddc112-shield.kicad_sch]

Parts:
C1: 0.47uF; C_0805_2012Metric_Pad1.18x1.45mm_HandSolder
C2, C7: 0.33uF; C_0805_2012Metric_Pad1.18x1.45mm_HandSolder
C3, C5, C6, C8, C10, C12, C14: 0.1uF; C_0805_2012Metric_Pad1.18x1.45mm_HandSolder
C4, C9, C11, C13: 10uF; C_0805_2012Metric_Pad1.18x1.45mm_HandSolder
C19, C20: C; C_0805_2012Metric_Pad1.18x1.45mm_HandSolder
D1, D2, D3: LED; PinHeader_1x02_P2.54mm_Vertical
J1: Screw_Terminal_01x02; TerminalBlock_MaiXu_MX126-5.0-02P_1x02_P5.00mm
J2, J3: Conn_01x02; PinHeader_1x02_P2.54mm_Vertical
J4: Power; PinSocket_1x08_P2.54mm_Vertical
J5: Analog; PinSocket_1x06_P2.54mm_Vertical
J6: Digital/PWM; PinSocket_1x10_P2.54mm_Vertical
J7: Digital/PWM; PinSocket_1x08_P2.54mm_Vertical
R1: 10k; R_0805_2012Metric_Pad1.20x1.40mm_HandSolder
R2: 0R; R_0805_2012Metric_Pad1.20x1.40mm_HandSolder
R8, R9: 4.7k; R_0805_2012Metric_Pad1.20x1.40mm_HandSolder
U1: REF3040; SOT-23
U2, U4: L78L05_SOT89; SOT-89-3
U3: OPA350; SOIC-8_3.9x4.9mm_P1.27mm
U5: DDC112; SOIC-28W_7.5x17.9mm_P1.27mm

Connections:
+3V3: J4.4
+5V: J4.5
/AREF: J6.3
/IOREF: J4.2
/LED_driver/LED_1: D1.2 (A); also elsewhere on the board
/LED_driver/LED_2: D2.2 (A); also elsewhere on the board
/LED_driver/LED_3: D3.2 (A); also elsewhere on the board
/LED_driver/LED_K: D1.1 (K), D2.1 (K), D3.1 (K); also elsewhere on the board
/PB0: J6.10, U5.12 (~DXMIT)
/PB1/OC1A: J6.9, U5.9 (CONV)
/PB2/SS: J6.8
/PB3/MOSI: J6.7, U5.13 (DIN)
/PB4/MISO: J6.6, U5.16 (DOUT)
/PB5/SCLK: J6.5, U5.11 (DCLK)
/PC0/ADC0: J5.1, U5.18 (RANGE0)
/PC1/ADC1: J5.2, U5.19 (RANGE1)
/PC2/ADC2: J5.3, U5.20 (RANGE2)
/PC3/ADC3: J5.4
/PC4/SDA/ADC4: J5.5, J6.2, R9.2; also elsewhere on the board
/PC5/SCL/ADC5: J5.6, J6.1, R8.2; also elsewhere on the board
/PD0/TXD: J7.8
/PD1/TXD: J7.7
/PD2: J7.6
/PD3: J7.5
/PD4: J7.4
/PD5: J7.3, U5.8 (TEST)
/PD6/OC0A: J7.2, U5.10 (CLK)
/PD7: J7.1, U5.17 (~DVALID)
/VREF: C11.1, C12.1, U3.1, U3.2 (-), U5.22 (VREF)
/Vin: J4.8
/~RESET: J4.3
GND: C7.2, C8.2, C13.2, C14.2, J1.2, J4.6, J4.7, J6.4, R2.1, U4.2 (GND), U5.15 (DGND); also elsewhere on the board
unnamed: C19.1, U5.5 (CAP1A)
unnamed: C19.2, U5.4 (CAP1B)
unnamed: C20.1, U5.24 (CAP2A)
unnamed: C20.2, U5.25 (CAP2B)
unnamed: J2.1, U5.1 (IN1)
unnamed: J3.1, U5.28 (IN2)
unnamed: R1.1, U1.2 (OUT)
unnamed: C4.1, C5.1, R1.2, U3.3 (+)
VBUS: C2.1, C7.1, J1.1, U2.3 (IN), U4.3 (IN)
VCC: C8.1, C13.1, C14.1, R8.1, R9.1, U4.1 (OUT), U5.14 (DVDD)

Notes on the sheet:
PHOTODIODE INPUTS
UNO Shield
VREF per datasheet
9V POWER
BU BOTLAB
Photodiode ADC (DDC112) Evaluation board (Arduino shield)

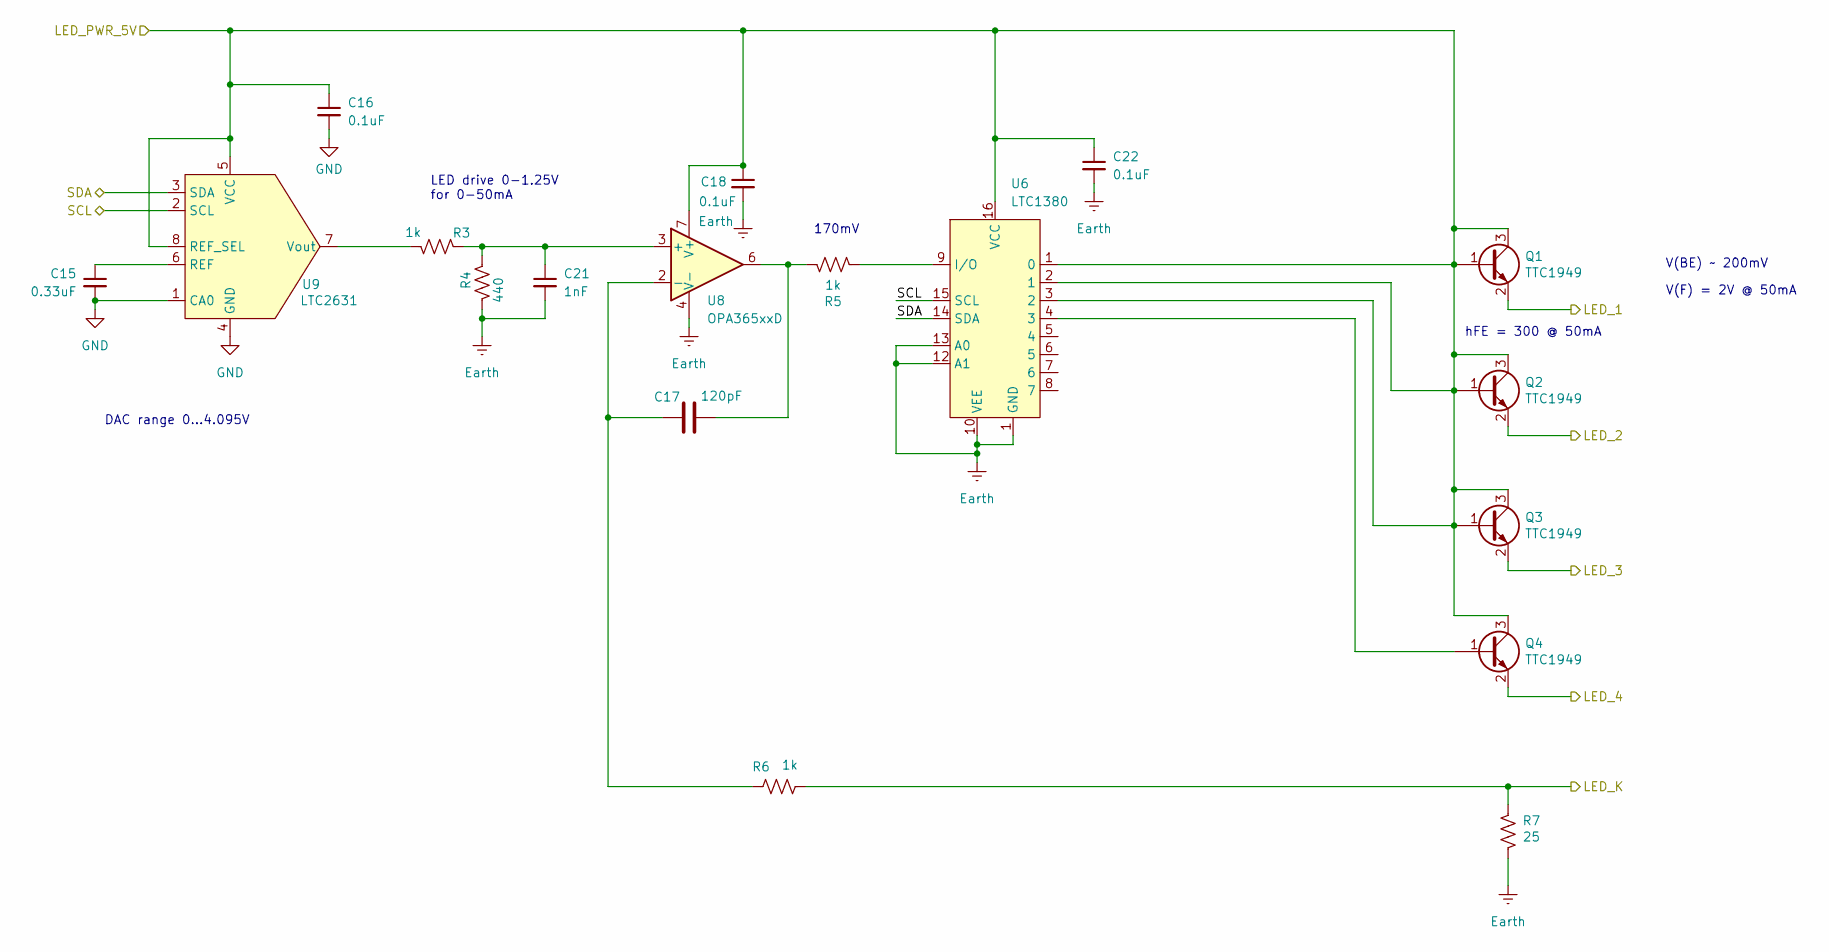
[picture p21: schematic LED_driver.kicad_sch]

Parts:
C15: 0.33uF; C_0805_2012Metric_Pad1.18x1.45mm_HandSolder; DigikeyNumber 1276-2048-1-ND
C16, C22: 0.1uF; C_0805_2012Metric_Pad1.18x1.45mm_HandSolder; DigikeyNumber 1276-1005-1-ND
C17: 120pF; C_0805_2012Metric_Pad1.18x1.45mm_HandSolder
C18: 0.1uF; C_0805_2012Metric_Pad1.18x1.45mm_HandSolder
C21: 1nF; C_0805_2012Metric_Pad1.18x1.45mm_HandSolder
Q1, Q2, Q3, Q4: TTC1949; SC-59; DigikeyNumber TTC1949-GRLFCT-ND
R3, R5, R6: 1k; R_0805_2012Metric_Pad1.20x1.40mm_HandSolder
R4: 440; R_0805_2012Metric_Pad1.20x1.40mm_HandSolder
R7: 25; R_1206_3216Metric
U6: LTC1380; SOIC-16_3.9x9.9mm_P1.27mm; DigikeyNumber 505-LTC1380CS#PBF-ND
U8: OPA365xxD; SOIC-8_3.9x4.9mm_P1.27mm
U9: LTC2631; TSOT-23-8; DigikeyNumber LTC2631CTS8-HZ12#TRMPBFCT-ND

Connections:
/LED_driver/LED_1: Q1.2 (E); also elsewhere on the board
/LED_driver/LED_2: Q2.2 (E); also elsewhere on the board
/LED_driver/LED_3: Q3.2 (E); also elsewhere on the board
/LED_driver/LED_4: Q4.2 (E)
/LED_driver/LED_K: R6.1, R7.2; also elsewhere on the board
/PC4/SDA/ADC4: U6.14 (SDA), U9.3 (SDA); also elsewhere on the board
/PC5/SCL/ADC5: U6.15 (SCL), U9.2 (SCL); also elsewhere on the board
GND: C15.2, C16.2, U9.1 (CA0), U9.4 (GND); also elsewhere on the board
unnamed: C17.2, R5.2, U8.6
unnamed: Q4.1 (B), U6.4 (3)
unnamed: R5.1, U6.9 (I/O)
unnamed: C21.1, R3.1, R4.1, U8.3 (+)
unnamed: C17.1, R6.2, U8.2 (-)
unnamed: C15.1, U9.6 (REF)
unnamed: R3.2, U9.7 (Vout)

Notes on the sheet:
DAC range 0...4.095V
LED drive 0-1.25V for 0-50mA
V(BE) ~ 200mV
170mV
V(F) = 2V @ 50mA
hFE = 300 @ 50mA

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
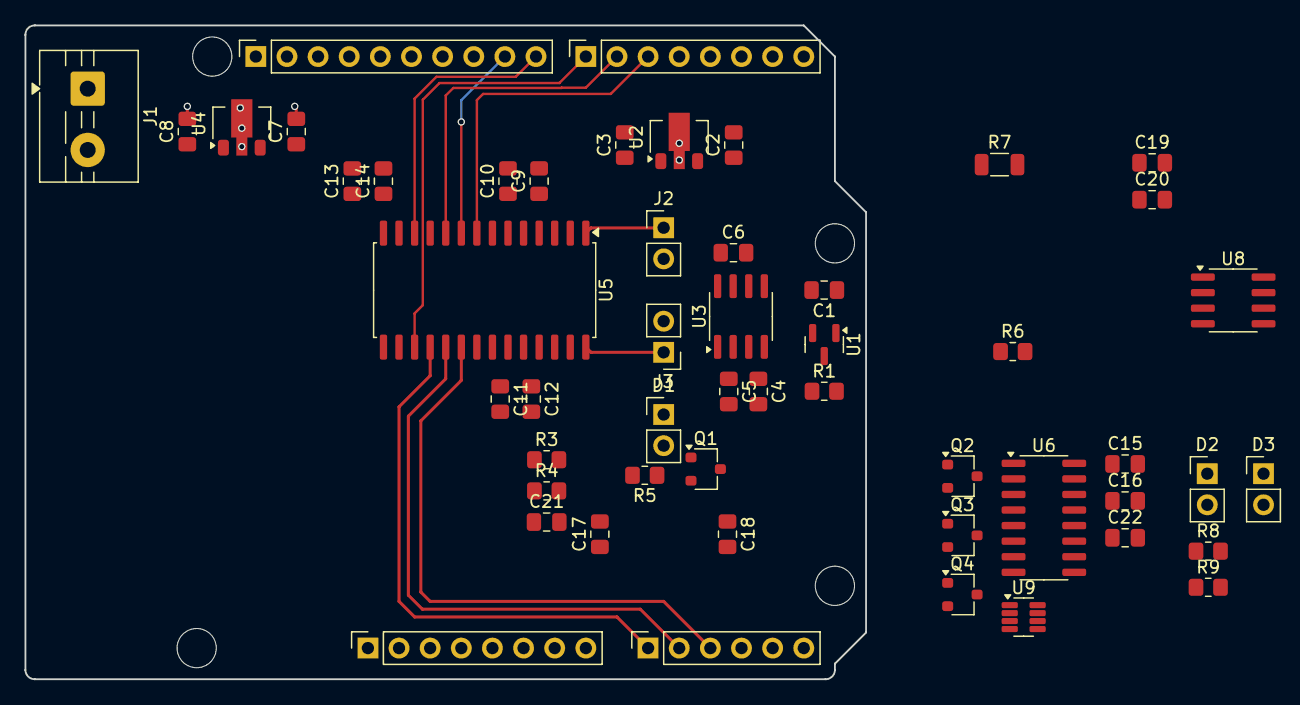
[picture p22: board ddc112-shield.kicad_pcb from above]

Board: 4 copper layers, 68.6 x 53.3 mm, 57 parts (1 on the bottom side), 38 nets.

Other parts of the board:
MH1, MH2, MH3, MH4: MountingHole_3.2mm

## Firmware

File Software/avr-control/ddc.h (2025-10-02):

#ifndef DDC_H_INCLUDED
#define DDC_H_INCLUDED

#define DCLK_PORT PORTB
#define DCLK_DDR DDRB
#define DCLK_PIN PINB

#define DCLK_BIT PB5
#define DIN_BIT PB3
#define DOUT_BIT PB4
#define DXMIT_BIT PB0
#define CONV_BIT PB1

#define DVALID_PORT PORTD
#define DVALID_DDR DDRD
#define DVALID_PIN PIND
#define DVALID_BIT PD7

#define TEST_PORT PORTD
#define TEST_DDR DDRD
#define TEST_PIN PIND
#define TEST_BIT PD5
#define TEST_MASK _BV(TEST_BIT)

#define RANGE_PORT PORTC
#define RANGE_DDR DDRC
#define RANGE_MASK 7

#ifdef UNO_TARGET
#define LED_PORT PORTB
#define LED_DDR DDRB
#define LED_BIT PB5
#define LED_MASK _BV(LED_BIT)
#endif

#ifdef AVR_TARGET
#define LED_PORT PORTD
#define LED_DDR DDRD
#define LED_MASK (_BV(PD2)|_BV(PD3))
#define LED_BIT PD2
#define LED2_BIT PD3
#endif

void ddc_init();
void ddc_range(uint8_t r);
void ddc_leds(uint8_t v);
int wait_for_dvalid();
int wait_for_dvalid_conv();
uint32_t* read_ddc();

#endif

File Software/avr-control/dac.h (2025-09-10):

#include "i2c.h"
#include <stdint.h>

// registers on LT2631
#define DAC_WINPUT 0
#define DAC_UPDATE 1
#define DAC_WR_AND_UPDATE 3
#define DAC_PWR_DOWN 4
#define DAC_SEL_INT_REF 6
#define DAC_SEL_EXT_REF 7

uint8_t set_dac( uint16_t v);

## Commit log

2025-08-06 starting on schematic
    [ddc112-shield.kicad_pcb, ddc112-shield.kicad_sch]
2025-08-06 working on schematic
    [ddc112-shield.kicad_sch]
2025-08-06 initial schematic; test software
    [ddc112-shield.kicad_pcb, ddc112-shield.kicad_sch]
2025-08-06 placement adjust
    [ddc112-shield.kicad_pcb]
2025-08-14 starting on LED driver
    [LED_driver.kicad_sch, SensorBoard.dxf, ddc112-shield.kicad_pcb, ddc112-shield.kicad_sch]
2025-08-15 woring on LED driver
    [#SensorBoard.dxf, LED_driver.kicad_sch, ddc112-shield.kicad_sch]
2025-08-15 LED driver schematic complete?
    [LED_driver.kicad_sch, ddc112-shield.kicad_pcb, ddc112-shield.kicad_sch]
2025-08-16 working on BOM
    [LED_driver.kicad_sch, led-photodiode-avr-B_Cu.gbr, led-photodiode-avr-B_Mask.gbr, led-photodiode-avr-B_Silkscreen.gbr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]
2025-08-16 many schematic tweaks; add fields for BOM
    [LED_driver.kicad_sch, led-photodiode-avr.kicad_pcb, led-photodiode-avr.kicad_sch]
2025-08-16 routing done
    [LED_driver.kicad_sch, led-photodiode-avr.kicad_pcb, led-photodiode-avr.kicad_sch]
2025-08-17 ready for review
    [LED_driver.kicad_sch, led-photodiode-avr-B_Cu.gbr, led-photodiode-avr-B_Mask.gbr, led-photodiode-avr-B_Silkscreen.gbr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]
2025-08-17 ready for review (update PDF, gerber)
    [led-photodiode-avr.kicad_sch]
2025-08-17 add 3D models, optical board
    [LED_MTE9730.step, Photodiode.step, optical-carrier.kicad_pcb, optical-carrier.kicad_sch]
2025-08-18 small tweaks
    [282836-2.step, OptodeCell_081425.STL, led-photodiode-avr.kicad_pcb, led-photodiode-avr.kicad_sch]
2025-08-25 V1.0 as built
    [led-photodiode-avr-B_Cu.gbr, led-photodiode-avr-B_Mask.gbr, led-photodiode-avr-B_Silkscreen.gbr, led-photodiode-avr-Edge_Cuts.gbr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]
2025-08-26 update LED command and add range command
2025-09-10 DAC and MUX working, LED output OK
2025-09-11 readout working
    [LED_driver.kicad_sch]
2025-10-14 more tests
    [adc_box.scad, adc_box.stl, adc_lid.stl, led-photodiode-avr.kicad_pcb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]
2025-10-15 Add temperature readout
